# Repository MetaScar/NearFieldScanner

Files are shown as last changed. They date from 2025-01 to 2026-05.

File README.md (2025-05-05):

# Overview

Welcome to the low cost planar near-field scanner repo! 
The goal of this repo is to contain everything you will need to build your own near-field scanner.
Everything in this repo is open source under the Apache 2 license. Feel free to modify as needed, but reference this repo.

Instructions for how to build the near-field scanner are not yet complete. 
However, all the required parts for building the near-field scanner should be listed or an stl file provided to allow the user to 3D print their own parts.
Details on manufacturing these parts are not yet provided.

If you are interested in manufacturing your own near-field scanner, feel free to contact Jacob Stewart at jast5436@colorado.edu.

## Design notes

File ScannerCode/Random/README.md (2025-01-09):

Date: 2025-01-09
This folder is the result of organizing the code significantly later than when the code was created. This is random code with likely little importance to the end user. It is put here just in case the user is interested in looking.

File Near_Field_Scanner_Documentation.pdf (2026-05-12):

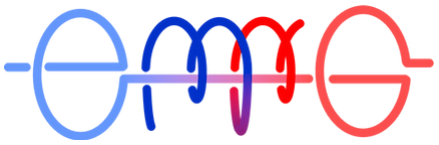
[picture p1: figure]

# Near Field Scanner Documentation

## Version 0.2

## Jacob Stewart

## Edited by Ellis Johnson

May 12, 2026

## Contents

### 1 Introduction | 2

### 2 Quickstart | 2

2.1 Common GRBL Commands | 2

### 3 Hardware | 2

3.1 General Comments | 2
3.2 Gantry System | 2
3.3 Panel Connection | 3
3.4 Circuit Design | 4
3.5 The Arduino Uno (GRBL) | 5
3.6 Cable Connections | 7
3.7 Comments and Improvements | 7

### 4 Software | 9

4.1 Definitions | 9
4.2 GRBL Commands | 9

### 5 Background Theory | 11

5.1 Near to Far Field Criteria | 11

### 6 Appendix | 11

6.1 GRBL Settings | 11

## List of Code Listings

# 1 Introduction

This documentation will cover the basics of how to use the near field scanner, how the hardware is configured, and how the software is configured. The hardware section will cover important things to note about the construction of the machine. Information that can likely be quickly understood by some quick analysis of the machine will probably be left out of the documentation.

# 2 Quickstart

## 2.1 Common GRBL Commands

# 3 Hardware

## 3.1 General Comments

Much of the design is based around CNC machines. The custom parts that deviate from this basic design (the panel and its connections, for example) will be covered in this manual.

The primary functions/aspects of the hardware are the GRBL Arduino Uno R3 controller, which controls the hardware for the gantry system, which holds and controls the position of the probe. The AUT is simply attached to an acrylic table.

## 3.2 Gantry System

The majority of the hardware components were purchased from OpenBuilds¹ (https://openbuildspartstore.com/)
. The remaining parts were likely custom designed. Parts can be found in the Microsoft Teams’ Near Field Scanner > Models folder.

1 https://openbuildspartstore.com/

Each of the linear rails can be constructed following this guide² (https://youtu.be/tLozVt_CjXQ?si=yefkdUC8tTgpIad6)
, which
demonstrates how to build a smaller version of the 1 meter (https://youtu.be/tLozVt_CjXQ?si=yefkdUC8tTgpIad6) linear actuators.

There are only two unique connections in the gantry system. The first is between the machine y-axis (the bar running between the parallel x-axis). Before making this connection, assemble the gantry plates, and attach them to the y-axis C-Beam. With how the x-axis C-Beams are attached to the wooden base, the gantry plates should be connected approximately 5 mm from the edges. Instead of tightening the attachment between the gantry plates and the y-axis C-Beam, keep them loose as you line up the gantry plates into the channels of the x-axis C-Beams. Unfortunately, the x-axis C-Beams are not perfectly parallel, so it is likely best to line up the gantry plates near the center of the x-axis C-Beams. Once the gantry plates are lined up to a satisfactory degree, you can tighten them in and run the lead screws through the gantry plates.

The other unique connection is between the gantry plate of the y-axis and the z-axis C-Beam. This requires a custom part, which is 3D printed from the “2 Become 1" model. There is a design for the smaller gantry plate and the larger gantry plate. For either plate, it is recommended to 3D print using and FDM printer. Though an SLA printer is more accurate, it also has a tendency to warp large flat surfaces. Additionally, the cost of SLA resin is much greater than FDM PLA filament.

Once the “2 Become 1" connector is printed, you must first attach the connector to the z-axis C-Beam. The screwing holes and method is the same as the C-Beam end mount. After the connector and the C-Beam are connected, you can attach the connector the y-axis gantry plate. You may want to ask for an assistant to hold the z-axis C-Beam while you are attaching the connector to the y-axis gantry plate.

## 3.3 Panel Connection

Many of the components for the panel system are removable. Unfortunately, in order to remove the panel completely from the z-axis gantry plate, nearly all the components must be disassembled one after

2 https://youtu.be/tLozVt_CjXQ?si=yefkdUC8tTgpIad6 the other. Those components include the “connect to panel" connector, the absorber, the acrylic panel, and the panel to z-axis connector.

In order to remove the panel, the absorber will need to be removed first. It is advised that two people work together to remove the absorber. It is also advised to wear gloves when handling absorber, as it can act as an irritant. To remove the absorber, carefully peel the velcro along the edges. When removing the absorber, something to avoid is damaging the absorber spikes.

These are fragile, and vital to the absorber’s performance. With this in mind, it is slightly better to start peeling the absorber from the velcro along the bottom edge and work your way up. If you were to drop the absorber while removing it from bottm to top, it is more likely to fall on the flat back of the absorber rather than the spiky front.

After the absorber has been removed, the acrylic panel can be unscrewed from the panel to z-axis connector. Once the acrylic panel has been removed and set aside, the panel to z-axis connector can be unscrewed and removed.

In order to remove the “connect to panel" connector, the absorber will need to be removed first, as described above. Though you can remove this part, it isn’t necessary. It is designed to remain attached, and instead provide screw holes for different probe to panel mounts. Each of these probe to panel mounts will have to be custom designed around the probe being connected. Each of these screw holes are evenly spaced 1.125 inches away from each other. An example 3D model of this part can be found in the “Probe to Panel Mount" file on Microsoft Teams.

Reassembly of the panel is mostly the same as removal in reverse. In particular, it is easier to install the absorber by connecting the velcro at the top of the panel, and work your way down, allowing the top connection to act as a hinge to swing the absorber into the remaining velcro connections.

## 3.4 Circuit Design

A wiring diagram can be found in Figure 1. Though the wiring may look like a complicated mess, if you look closely, the mess is a consequence of the amount of wires more than the complexity of the circuit. Most of

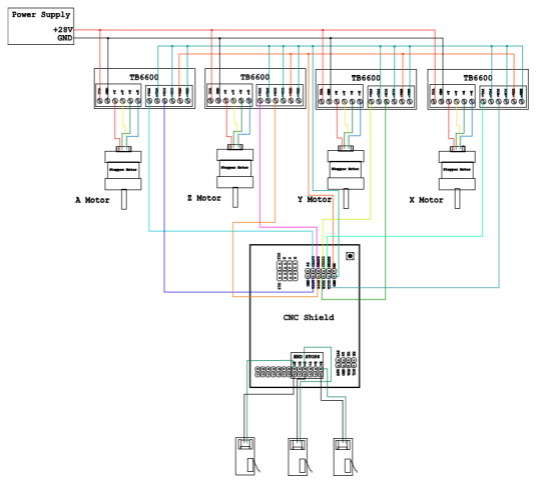
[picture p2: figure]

Figure 1: The CNC Wiring Schematic. Wire colors loosely match real wire colors, but are not perfectly equivalent.

the connections between the stepper drivers (the TB6600s) and the CNC Shield are for the CNC Shield’s ground pin.

As for the PCB design, the complete design file can be found in the Microsoft Teams folder in the file “PCB Wiring".

## 3.5 The Arduino Uno (GRBL)

The Arduino Uno is running a firmware called GRBL³ (https://github.com/gnea/grbl)
, which is a CNC
firmware that is practically the standard firmware for maker movement devices. Many 3D printers run GRBL under the hood. It is strongly advised to use an Arduino Uno R3 with a 16U2 communication chip rather than a CH340 chip. If you have the official Arduino Uno R3, you have the 16U2 communication chip. If you are not sure which chip your board has, it can be visually determined. On an official Arduino Uno R3, the 16U2 is the square surface mounted chip just behind the USB type-B port. On a board with a CH340 communication chip, in a similar location to the 16U2 chip, there will be a larger rectangular surface mounted chip.

3 https://github.com/gnea/grbl

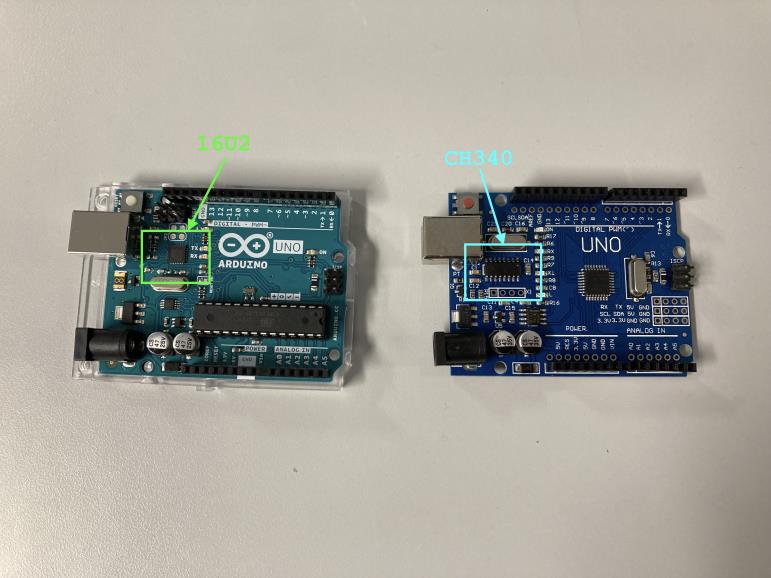
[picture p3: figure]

Figure 2: A visual comparison between the 16U2 chip and the CH340 chip. It is strongly advised to use an Arduino Uno R3 with the 16U2 chip.

When flashing the firmware to the Arduino Uno R3, there are two essential changes that need to be made to the GRBL configuration file. To make these changes, first follow the offical Compiling Grbl (https://github.com/gnea/grbl/wiki/Compiling-Grbl) 4 instructions up until step 5: “Compile and upload Grbl to your Arduino" for Arduino IDE 1.x, or until step 12 for Arduino IDE 2.x. At this point, the Grbl code has been added to your Arduino library.

In this library is the compilation configuration file. The essential changes will be made here. This file can be accessed by going to
WindowsUser/Documents/Arduino/libraries/grbl/config.h. | (Note | that
this location may change between your computer’s OS, the version of Arduino, etc. If you are unable to find the library, an internet search should allow for you to find the library location). For the first essential
change, | go | to | line | 124, | and | uncomment | #define
HOMING_SINGLE_AXIS_COMMANDS. For the second essential change, go to line 339 and comment out #define VARABLE_SPINDLE.

The first change is necessary because it enables commands that allow for each axis to be homed one at a time ($HX, $HY, $HZ). Homing each

4 https://github.com/gnea/grbl/wiki/Compiling-Grbl axis one at a time is more reliable than using the default in homing command $H. Thus, the Matlab code uses and requires these commands. The second change is necessary due to the CNC Shield in use. The newer version of GRBL uses pin D12 of the Arduino Uno rather than pin D11 for the Z-Axis limit switch. This is because the newer version of GRBL needs the PWM variable voltage output of D11 for a new feature to control a variable spindle. However, older versions of GRBL (which this CNC Shield had in mind) use pin D11 for the Z-Axis limit switch. Because this machine does not have a variable spindle and needs the Z-Axis limit switch, line 339 of the configuration file should be commented out to reenable pin D11 as the limit switch pin.

Once these configuration comments have been altered, you can flash the firmware.

After the firmware has been flashed, the GRBL settings need to be correctly configured. Open a serial connection with GRBL (for example, through the Arduino IDE) and check what settings are currently in use by the GRBL by entering $$. Change the settings as needed – the required settings can be found in Appendix 6.1. More information about the settings and how to change them can be found in the GRBL wiki⁵ (https://github.com/gnea/grbl/wiki/Grbl-v1.1-Configuration#grbl-settings) .

## 3.6 Cable Connections

There are two different connections that need to be made in order for the gantry system to be controlled. The first is the USB connection between the Arduino Uno R3 and the computer. This allows for the serial connection between the Arduino Uno and the computer for GRBL command communication. This also powers the Arduino Uno.

The second connection is the Cincon 28V AC power adapter. This connects between a wall outlet and the DC power jack on the wiring PCB. This powers the four TB6600 stepper drivers.

## 3.7 Comments and Improvements

Though the linear actuators⁶ (https://openbuildspartstore.com/c-beam-linear-actuator-bundle/) used for the gantry system are a cost effective method of getting a (approximately) millimeter precise machine,

5 https://github.com/gnea/grbl/wiki/Grbl-v1.1-Configuration# grbl-settings 6 https://openbuildspartstore.com/c-beam-linear-actuator-bundle/

they are not reliable as other methods. For example, a linear actuator combined with linear rails would be significantly more stable and reliable compared to just the linear actuator. With the inclusion of a feedback systems such as a PID control system, such a setup would likely be able to reach hundreds of micrometers of precision. Possibly even tens of micrometers. Such precision would allow for higher frequency measurements.

However, it is worth noting that such precision will not be necessary for the delta x criterion until frequencies above 200 GHz are being explored. Considering the hardware limitations of the VNA in use,

Another improvement would be the PCB design. The current design was made in house. For the sake of manufacturing convenience, vias were not added between the pins. Instead, the metal pins themselves were to act as the vias. To solder the top of the pin, solder paste was used. Unfortunately, the application and solidification of this solder paste was not very effective. This means the pins are incredibly susceptible to spontaneous disconnections. In other words, the PCB is not very reliable. This problem could be rectified by having a professional manufacture the PCB. As for a redesign, a PCB hat for the CNC shield would reduce the number of wire connections, keeping the package cleaner, more compact, and more reliable.

The AUT table is primarily lacking in one of the most important features for the table: its rigidity. The current design can easily be deflected, causing the entire table to oscillate. Fortunately, this oscillation is mostly caused by external forces, so while the machine is moving around when taking measurements, little oscillation occurs

The Z-Axis C-Beam also experiences a significant amount of wobble. The source of this wobble appears to be the gantry plate. A potential solution to this wobble would be to use a linear rail along the machine y-axis.

The power delivery method for the machine requires the user to manually plug and unplug the AC connector to wall power. It would be more convenient to power on the device with a switch. Along with this switch should be an emergency stop button which cuts power to the motors as soon as it is activated.

# 4 Software

## 4.1 Definitions

A confusing connection between the software and the hardware is the axis. In the software, you will see mentions of “machine x" or “code x". This is because what is the x-axis to the hardware (i.e., to GRBL) is different from the x-axis of the software. This is because much of the theory around transforming the near to far field of a planar near field scanner treats the distance between the probe and AUT as the z-axis, the horizontal motion between the probe and the AUT as the x-axis, and the height difference between the probe and the AUT as the y-axis. However, with how the hardware is configured, it is the x-axis that determines the distance between the probe and the AUT, the y-axis that determines the horizontal motion between the probe and the AUT, and the z-axis that determines the height difference between the probe and the AUT.

## 4.2 GRBL Commands

GRBL provides an explanation of the commands on the GRBL Wiki⁷ (https://github.com/gnea/grbl/wiki/Grbl-v1.1-Commands)
, and
though this manual will not cover all the commands, it will cover the most common ones used for this machine.

The first command the user will probably need to know is $X. This will unlock the machine, allowing the user to use subsequent commands to move the machine. The only other way to unlock the machine is with the homing commands.

If the user has followed the firmware flashing instructions in Hardware Section 3.5, then the special homing commands $HX, $HY, and $HZ can be used. These will home just their respective axis. Be careful when using this form of homing, as it will unlock the movement capabilities of the machine (same effect as $X) even if the other axis have not been homed. Thus, if your program requires all axis to be homed, either call all homing commands one after the other, or use the $H command (which has had spotty results for the current machine).

7 https://github.com/gnea/grbl/wiki/Grbl-v1.1-Commands

There are two basic homing commands: $G90 and $G91. Both of these commands have syntax in the form of:

$G91 X1 Y-2 Z3

(Quick Note: you don’t need to specify every axis every time you use the $G90 and $G91 commands. For example, $G91 X1 will only move the X axis, and will leave the Y and Z axis alone.)

The major difference between $G90 and $G91 is how it interprets the inputs for X1, Y2, and Z3. In the case of $G91, the machine is put into relative mode. This means if the user inputs X1, the machine will move the gantry system 1 unit in the positive X direction from its current X position. $G90, on the other hand, will move the machine to the absolute position where X = 1 unit. In the case of this particular machine, after the X axis has been homed, the absolute position is at -898.8 mm. This means that if the user were to input the command $G90 X1, the machine will attempt to ram the x-axis off the edge until it has “reached" the position at X = 1. In other words, it is generally much safer and easier for a person to use $G91 than it is to use $G90. However, absolute position is useful for programs and other aspects that don’t change between program reboots, such as the AUT position or the maximum and minimum positions of the axis.

Unfortunately, there doesn’t seem to be a command to stop the machine from making the current movement. Instead, the user will have to resort to hardware solutions, such as the ESTOP button on the PCB, or simply pulling the Arduino USB connection or pulling the power connection to the AC power supply connected to the PCB.

# 5 Background Theory

## 5.1 Near to Far Field Criteria

# 6 Appendix

## 6.1 GRBL Settings

The settings of the current GRBL setup after typing $$ into the GRBL serial prompt. More info on the GRBL settings can be found in the GRBL wiki⁸ (https://github.com/gnea/grbl/wiki/Grbl-v1.1-Configuration#grbl-settings)

Grbl 1.1h ['$' for help]
[MSG:'$H'|'$X' to unlock]
$0=10
$1=25
$2=0
$3=6
$4=0
$5=0
$6=0
$10=2
$11=0.010
$12=0.002
$13=0
$20=0
$21=0
$22=1
$23=3 $24=25.000
$25=500.000
$26=250
$27=1.000
$30=1000
$31=0
$32=0
$100=200.000

8 https://github.com/gnea/grbl/wiki/Grbl-v1.1-Configuration# grbl-settings

$101=200.000
$102=200.000
$110=500.000
$111=500.000
$112=500.000
$120=10.000
$121=10.000
$122=10.000
$130=900.000
$131=900.000
$132=900.000
ok

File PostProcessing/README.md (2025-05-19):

# Quickstart

The most powerful version of the post processing is contained in the `post_proc_nf_scan.m` Matlab file. By default, it uses the `NearFieldRawdata_Eravant_051525.mat` file located in the `./PostProcessing/Data/` directory. This file is provided in this GitHub repo as a link to a OneDrive as the file is around 600 MB (GitHub allows only a maximum of 100 MB before requiring [git-lfs](https://git-lfs.com/)). We do not use git-lfs due to our group's better familiarity with OneDrive compared to git.

With the post processing, the user can
- Time gate measurement by plotting both time and frequency domain
- Plot the near-field
- Plot the far-feild
- Plot the near-field radiation pattern to determine the phase center
- Plot the far-field radiation pattern 
- Plot 2D cuts at phi at 0, 45, and 90 degrees

Do be warned that the code can be quite memory hungry due to interpolation. To reduce memory usage by reducing interpolation, reduce the variable `N1q`.

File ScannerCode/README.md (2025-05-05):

Code related to or used by Professor Scarborough's Planar Near-Field Scanner. Majority of design and code created by Jacob Stewart. To communicate with a Keysight VNA, the code located in the "instrument" folder was created by Paul Flaten and Joel Johnson. Thank you for the code nerds!

# Quickstart
This quickstart guide is assuming you are trying to run the near-field scanner. This quickstart guide also assumes the user has arranged the antenna the user is testing (the AUT), and that the desired probe is installed. There is other code included in this repo that is used for just post processing the data located in the `./PostProcessing` directory. Hopefully, in a future version of the code, all post processing can be completed within the Matlab app. 

Because this guide is not exhaustive and perfect, if you think something is stupid/dangerous and you disagree with this guide, use your judgement. For example, if this guide does not tell you to wear an ESD strap while handling the VNA, but you think you should, use an ESD strap.

1. If you have not already, pull the git repo with desired method (using [GitHub Desktop](https://desktop.github.com/download/), the [terminal](https://github.com/git-guides/git-pull), etc.).
2. Start Matlab[^1], and turn on the VNA.
3. Inside Matlab, go to the directory of the git repo, then to `./ScannerCode`.
4. Inside Matlab, open `moveGUI.mlapp`. This is the Matlab app where the near-field scanner is controlled from.
5. The Matlab App Designer should have opened. Start the app by pressing the green play button up in the top left.
6. The app should be started. Now, plug in the Arduino Uno USB into the computer running the Matlab app and the <insert power block> into an outlet. If either does not seem to recieve power after plugging in, ensure the Arduino USB is connected to the USB-B port on the Arduino, and that the barrel connector is plugged into the PCB.
7. If you have not already, clear the space in and around the near-field scanner. It is about to start moving, so you don't want it to run into anything. Also, it is advised to unplug the probe and the AUT from the VNA, as future steps might cause electrical connections between the ports. Feel free to maintain the connection between the cable and the AUT/probe.
8. In the App, press the "Initialize" button in the top right. This will begin homing the machine.
9. Once the homing is completed and you have confirmed the completion, if this is the first time testing with the AUT positioned as it is now, you will need to run "Determine Z Dist" and "Find Probe Center". These will tell the program where the AUT is. If this has already been completed for the current setup, skip to step 12.
10. Click "Determine Z Dist". Follow the program, and use the controls to put the probe close to the AUT, and use a caliper to measure the physical distance between the probe and AUT. Write down the value provided by the program.
11. At the completion of "Determine Z Dist", you will be prompted to run "Find Probe Center". Go for it. Using the same controls, position the probe as close as possible to the center of the AUT. Write down the values provided by the program.
12. If you want the program to calculate the sampling criteria for a measurement, select "Determine Criteria". If you already have the criteria, skip this step.
13. Once you are ready to begin measuring, plug in the probe and AUT to the VNA.
14. Click "Run Measurement". The program will prompt you for anything it is missing, move to the center for one final check, then begin measuring.
15. At the completion of the measurements, you will be prompted to make a struct. This is advised, as variables such as the distance will be saved into the struct, which can be used later if you forgot how far the AUT was from the probe.
16. Once the measurement is complete, the data will be output to the `./ScannerCode/Data/` directory. Save this as preferred (e.g. USB drive, OneDrive, etc.).
17. Feel free to use the "Raw to Gated" program in the bottom right of the app to time gate your raw data, and "Raw to Struct" to turn the gated data into structs which can be used for plotting with the app's "Struct to Plots" program and transforming into the far field using the program `./PostProcessing/SimpleFarFieldTransform.m`.

# Data
It is not best practice to put your raw data files inside of git. Git is for tracking changes in text files. Instead, data files for the GitHub repo will be located in the [Microsoft Teams's `Files/Near Field Scanner/GitHubData` folder](https://o365coloradoedu.sharepoint.com/:f:/r/sites/ECEE-EMRG/Shared%20Documents/General/Near%20Field%20Scanner/GitHubData?csf=1&web=1&e=mdIfOC).
Folders named "Data" will be included in the git repo for the convenience of the user to put their own data. If there is data available in the Teams folder, it will be located in the same directory.
For example, the "Data" folder located at `./ScannerCode/Data/` is located at `/Near Field Scanner/GitHubData/ScannerCode` directory on Teams.

# Contact
Professor Cody Scarborough: cody.scarborough@colorado.edu

Jacob Stewart: jast5436@colorado.edu

Joel Johnson: jojo1082@colorado.edu

# Footnotes
[^1]: There are two different ways of starting Matlab apps. First, you do it through your file explorer without Matlab already opened. This will immediately open the app. The second is to open the app through Matlab's built in folder directory. In this case, the Matlab App Designer will also open up. This has the advantage of allowing the user to see the code (accessed by pressing "Code View" on the top right of the main window) and to see error messages. Because this code was made by an inept programmer and will likely produce many errors that require Matlab's error codes, it is advised to access the Matlab app through the Matlab App Designer.

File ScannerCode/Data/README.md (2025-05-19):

The current data files (M, O, S) are included as an example. You should not be including raw data in the git repo. 
This is enforced through the .gitignore file.

For the EMRG group, the data can be found in the [Teams Folder](https://o365coloradoedu.sharepoint.com/:f:/r/sites/ECEE-EMRG/Shared%20Documents/General/Near%20Field%20Scanner/GitHubData?csf=1&web=1&e=lnERgP).

Other teams/individuals are free to use [git-lfs](https://git-lfs.com/) or their own choice of file hosting to share the data files.

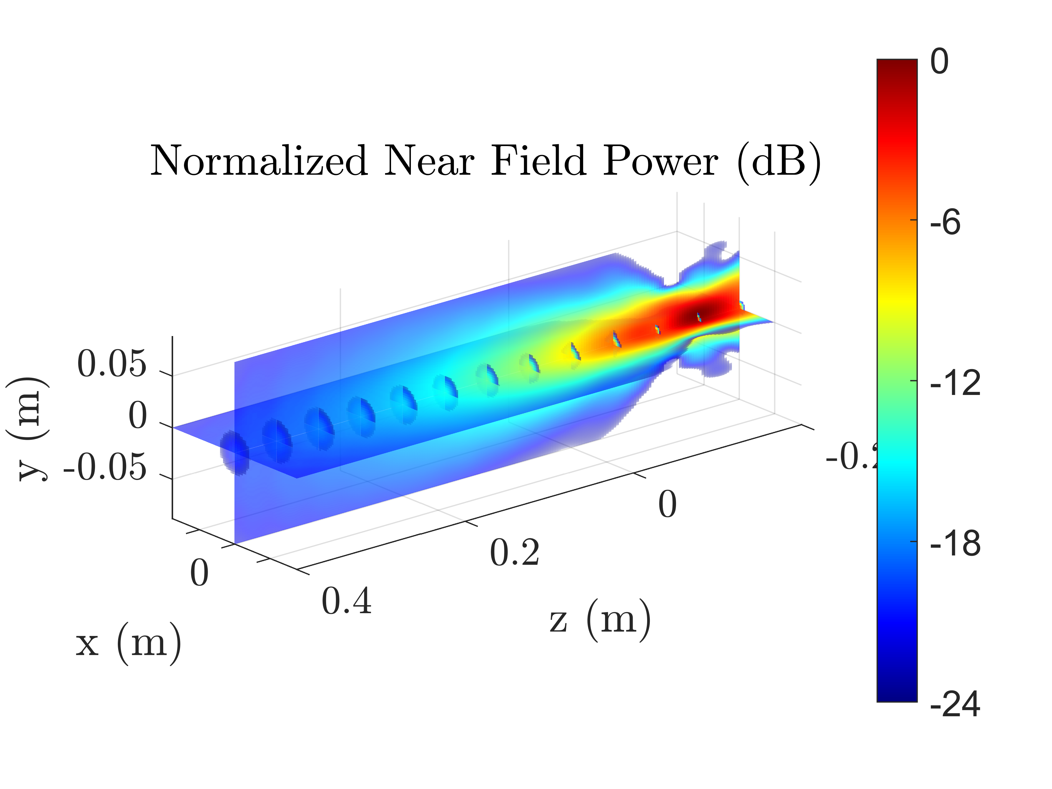
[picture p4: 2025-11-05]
PostProcessing/NearFieldProfile.png

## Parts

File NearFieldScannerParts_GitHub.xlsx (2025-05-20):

Item | Link | Number of units
WR90 open ended waveguide probe | https://www.ebay.com/itm/315099929331 | 1
Linear actuator (1m) | https://us.openbuilds.com/c-beam-linear-actuator-bundle/ | 3
10 ft mini circuit SMA cable | https://www.minicircuits.com/WebStore/dashboard.html?model=ULC-10FT-SMSM%2B | 1
6 ft mini circuit SMA cable | https://www.minicircuits.com/WebStore/dashboard.html?model=ULC-6FT-SMSM%2B | 1
Absorber: AEMi AEP-04 LG | https://www.mvg-world.com/en/products/absorbers/standard-absorbers/pyramidal-absorbers-aep-series | 1
CNC controller kit | https://www.amazon.com/Twotrees-Controller-Stepper-8-0%EF%BC%8CTB6600-Board%EF%BC%8CSwitch/dp/B08XNQTQXN | 1
40x40 Aluminum extrusion | https://us.openbuilds.com/v-slot-40x40-linear-rail/?searchid=0&search_query=aluminum+extrusion | 2
Aluminum extrustion corner brackets | https://www.mcmaster.com/products/aluminum-extrusion-gussets/t-slotted-framing-rail-profile~quad/rail-height~20-mm/ | 4
Acrylic sheet 24" x 24" | https://www.amazon.com/Acrylic-Plexiglass-Perspex-Transparent-Sheeting/dp/B07ZJM5GTP | 1
Arduino | https://store-usa.arduino.cc/products/arduino-uno-rev3?selectedStore=us | 1
Acrylic rods | https://www.amazon.com/FixtureDisplays%C2%AE-Diameter-Plexiglass-Transparent-10132-24/dp/B09T69KKSM?s=industrial | 4
M5 nuts | https://us.openbuilds.com/low-profile-screws-10-pack/ | 4
M5 Aluminum V nut pack | https://us.openbuilds.com/tee-nuts-m5-pack/ | 1
Drag Chains | https://www.amazon.com/Flexible-Connectors-Screwdriver-Engravers-Woodworking/dp/B09JCD362N | 2
1m V-Slot 40x40 | https://openbuildspartstore.com/v-slot-40x40-linear-rail/ | 2
Extended Open Gusset (5537T663) | https://www.mcmaster.com/products/aluminum-extrusion-gussets/t-slotted-framing-rail-profile~quad/rail-height~20-mm/ | 4

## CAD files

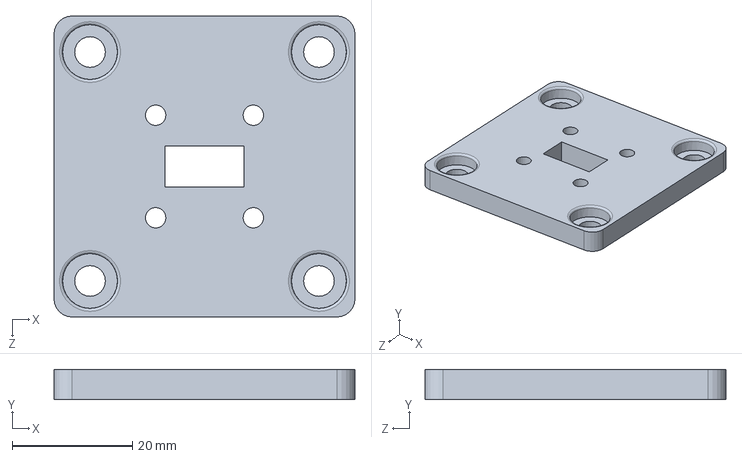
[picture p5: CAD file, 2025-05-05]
CAD/Original/Probe/WR42ProbeToPanelMount.SLDPRT
50.1 x 5.00 x 50.1 mm

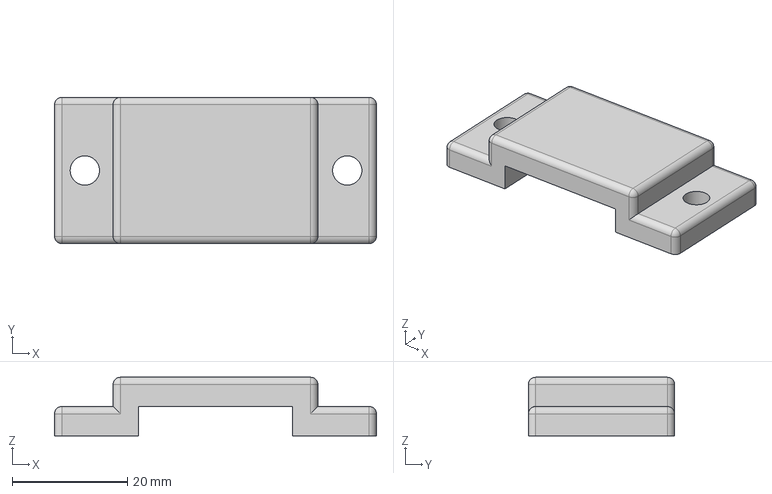
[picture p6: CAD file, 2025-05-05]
CAD/STEP/AUT/WR90GrabberTop.step
55.9 x 25.4 x 10.2 mm

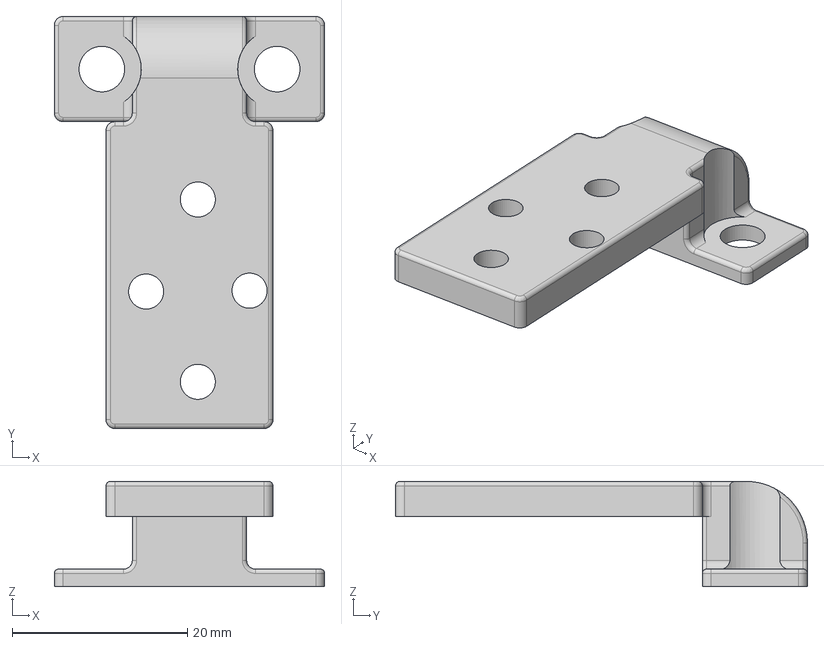
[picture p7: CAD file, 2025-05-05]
CAD/STEP/Wiring/XAxisDragChainConnector.step
30.8 x 47.0 x 12.0 mm

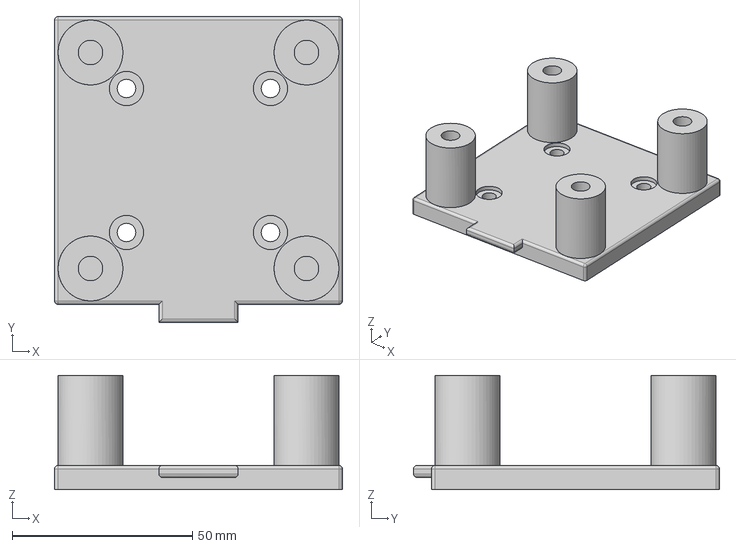
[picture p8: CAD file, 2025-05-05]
CAD/STEP/Z-AxisMount/ZAxisToPanel.step
80.0 x 85.0 x 31.7 mm
Panel

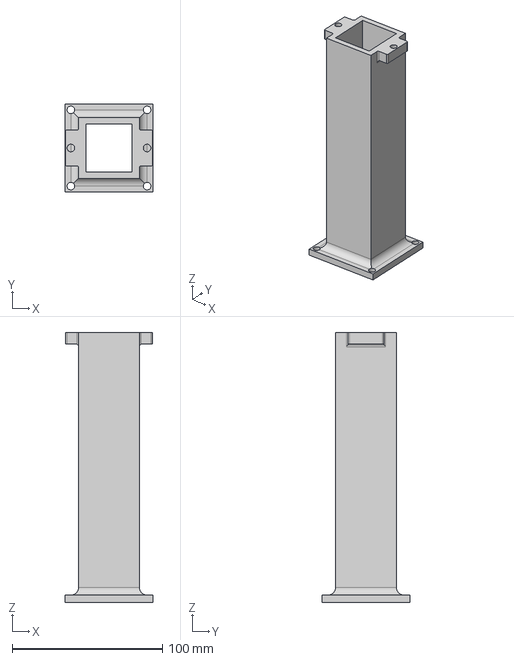
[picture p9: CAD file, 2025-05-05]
CAD/STEP/AUT/AUT Booster Seat v2.step
58.4 x 58.4 x 180.0 mm

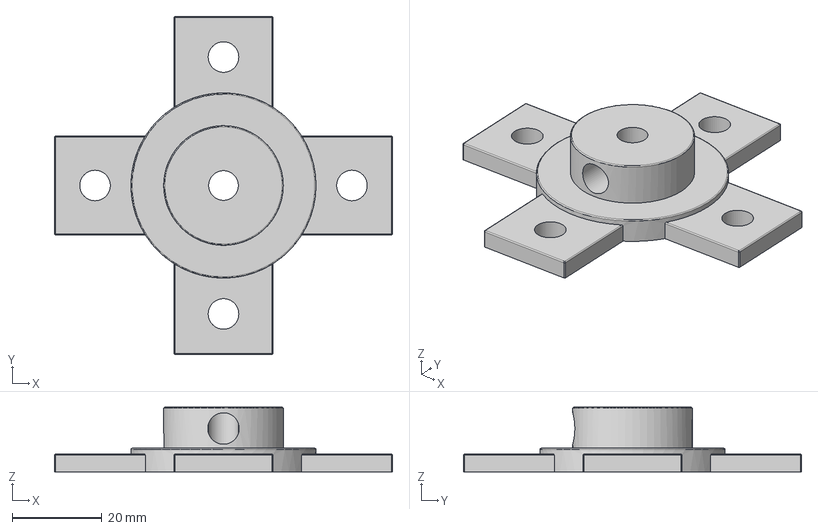
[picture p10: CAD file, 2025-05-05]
CAD/STEP/Probe/PigtailProbePanelMount.step
75.2 x 75.2 x 14.4 mm

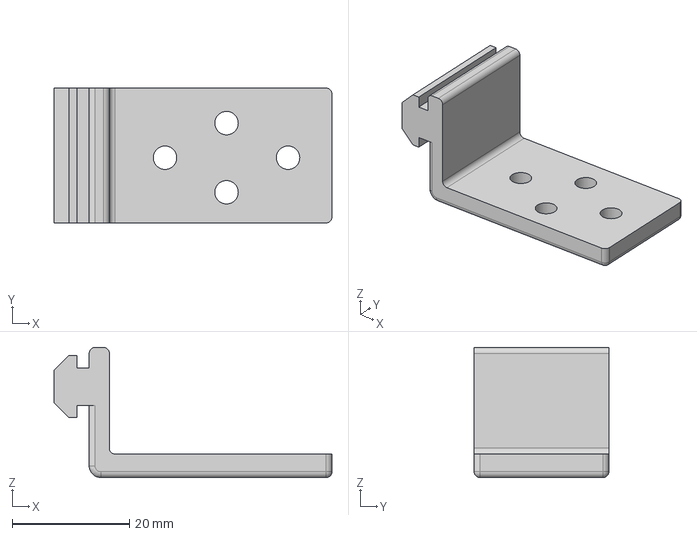
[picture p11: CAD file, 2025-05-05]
CAD/STEP/Wiring/YAxisDragChainHolder.step
47.5 x 23.0 x 22.2 mm

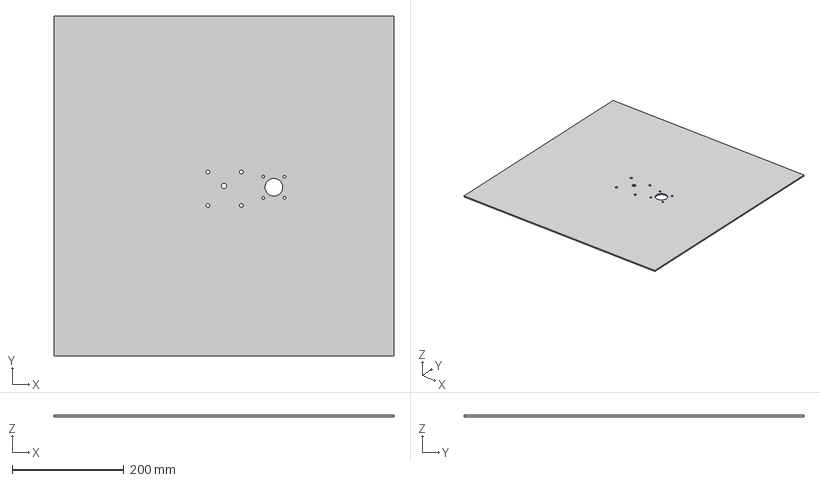
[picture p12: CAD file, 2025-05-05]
CAD/STEP/Z-AxisMount/AcrylicPanelCutout.step
609.6 x 609.6 x 3.18 mm

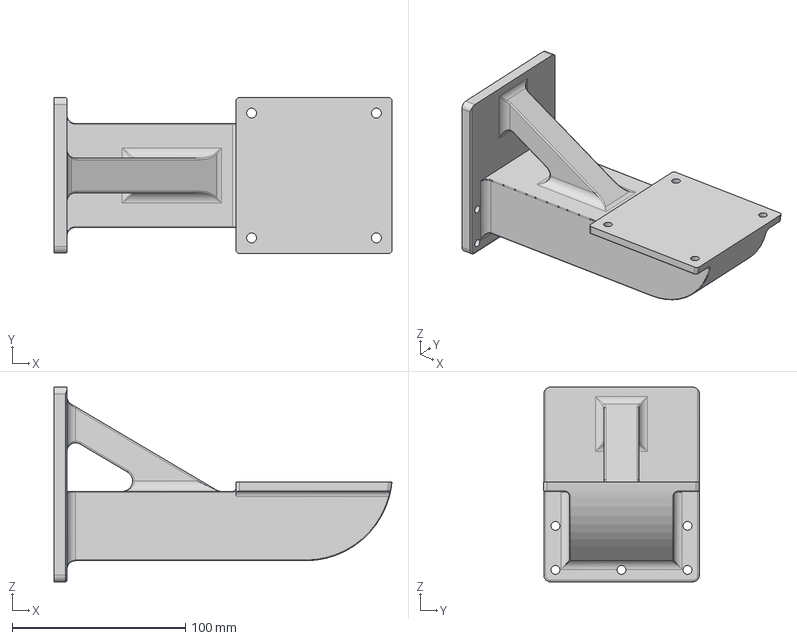
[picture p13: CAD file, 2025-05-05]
CAD/STEP/AUT/EravantAUTHolder v13.step
195.0 x 90.0 x 112.4 mm

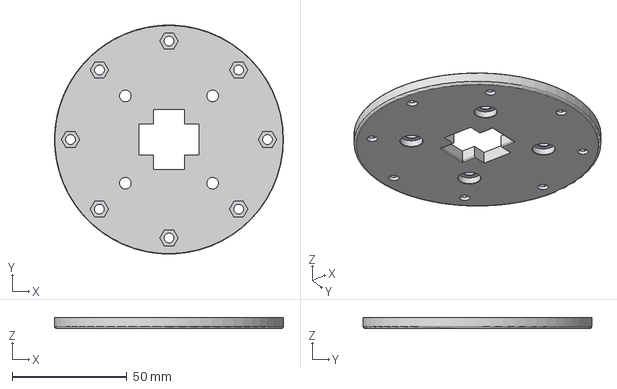
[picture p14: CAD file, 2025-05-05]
CAD/STEP/Probe/WR90OpenEndedWaveguideProbeMount.step
100.0 x 99.9 x 5.00 mm

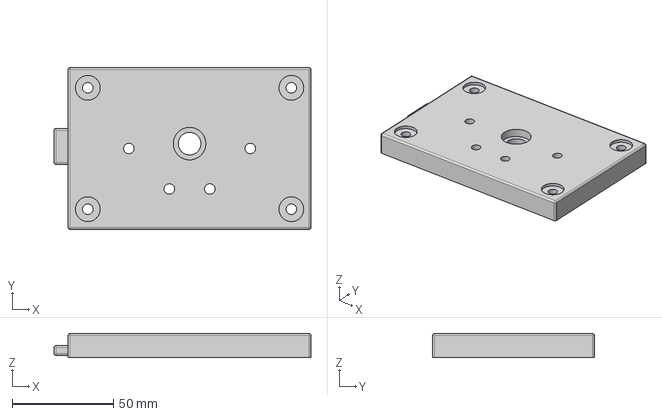
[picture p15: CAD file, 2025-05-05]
CAD/STEP/Z-AxisMount/Large 2 Become 1 v5.step
127.0 x 80.0 x 12.0 mm

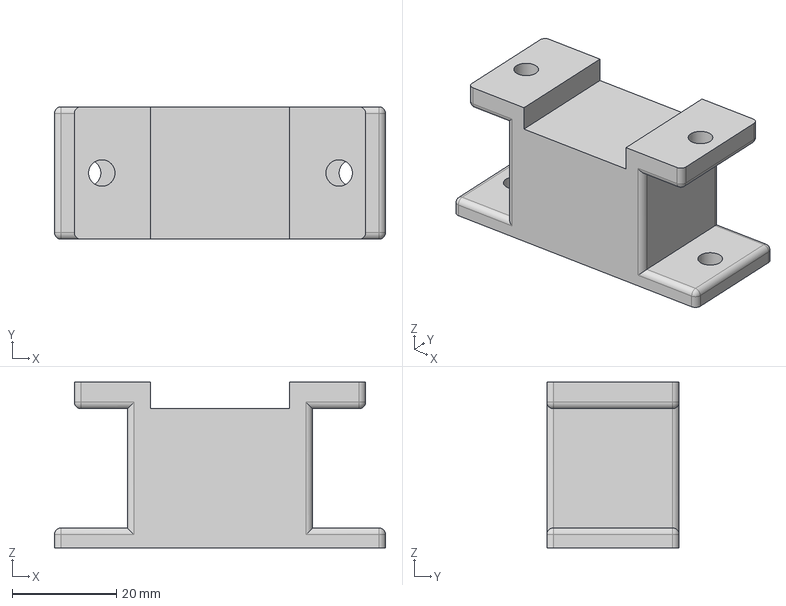
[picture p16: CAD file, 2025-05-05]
CAD/STEP/AUT/WR90GrabberBottom.step
63.5 x 25.4 x 31.8 mm

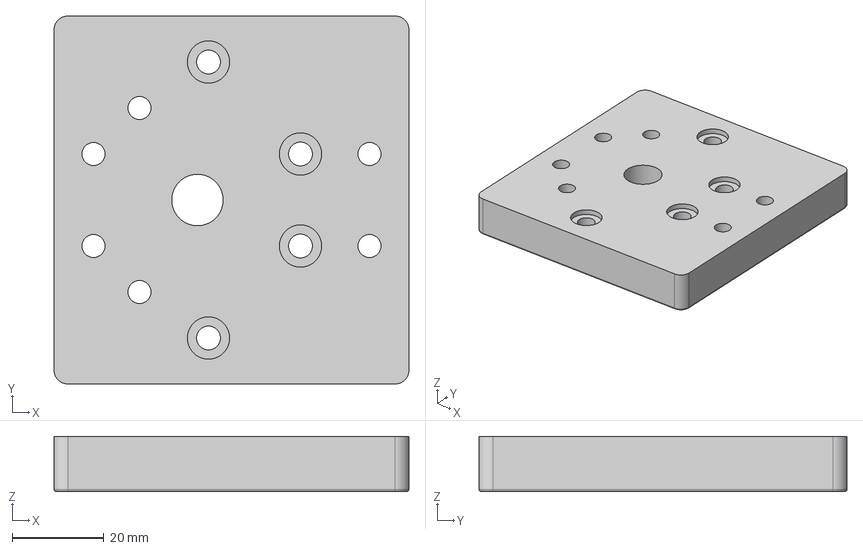
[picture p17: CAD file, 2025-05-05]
CAD/STEP/Z-AxisMount/2 Become 1 v9.step
77.2 x 80.0 x 12.0 mm

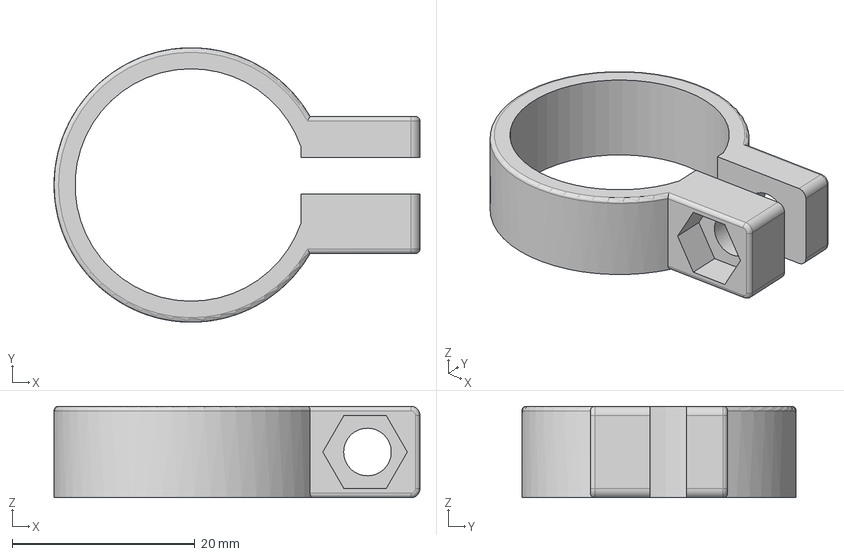
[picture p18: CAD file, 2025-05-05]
CAD/STEP/AUT/3D Shaft Collar v7.step
40.0 x 30.0 x 10.0 mm

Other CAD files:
CAD/STEP/Probe/WR42ProbeToPanelMount.STEP
CAD/Original/AUT/3D Shaft Collar v7.f3d
CAD/Original/AUT/AUT Booster Seat v2.f3d
CAD/Original/AUT/EravantAUTHolder v13.f3z
CAD/Original/AUT/WR90Grabber v6.f3z
CAD/Original/Probe/PigtailProbePanelMount.f3z
CAD/Original/Probe/Probe Mount Face On v27.f3z
CAD/Original/Probe/WR90OpenEndedWaveguideProbeMount.f3z
CAD/Original/Wiring/CableTrack v23.f3z
CAD/Original/Wiring/PCB Wiring v29.f3z
CAD/Original/Z-AxisMount/2 Become 1 v9.f3z
CAD/Original/Z-AxisMount/Large 2 Become 1 v5.f3z
CAD/STL/AUT/3D Shaft Collar v7.stl
CAD/STL/AUT/AUT Booster Seat v2.stl
CAD/STL/AUT/WR90GrabberBottom.stl
CAD/STL/AUT/WR90GrabberTop.stl
CAD/STL/Probe/PigtailProbePanelMount.stl
CAD/STL/Probe/WR42ProbeToPanelMount.STL
CAD/STL/Probe/WR90OpenEndedWaveguideProbeMount.stl
CAD/STL/Wiring/XAxisDragChainConnector.stl
CAD/STL/Wiring/YAxisDragChainHolder.stl
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

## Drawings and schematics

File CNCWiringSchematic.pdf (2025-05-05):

TB6600
TB6600

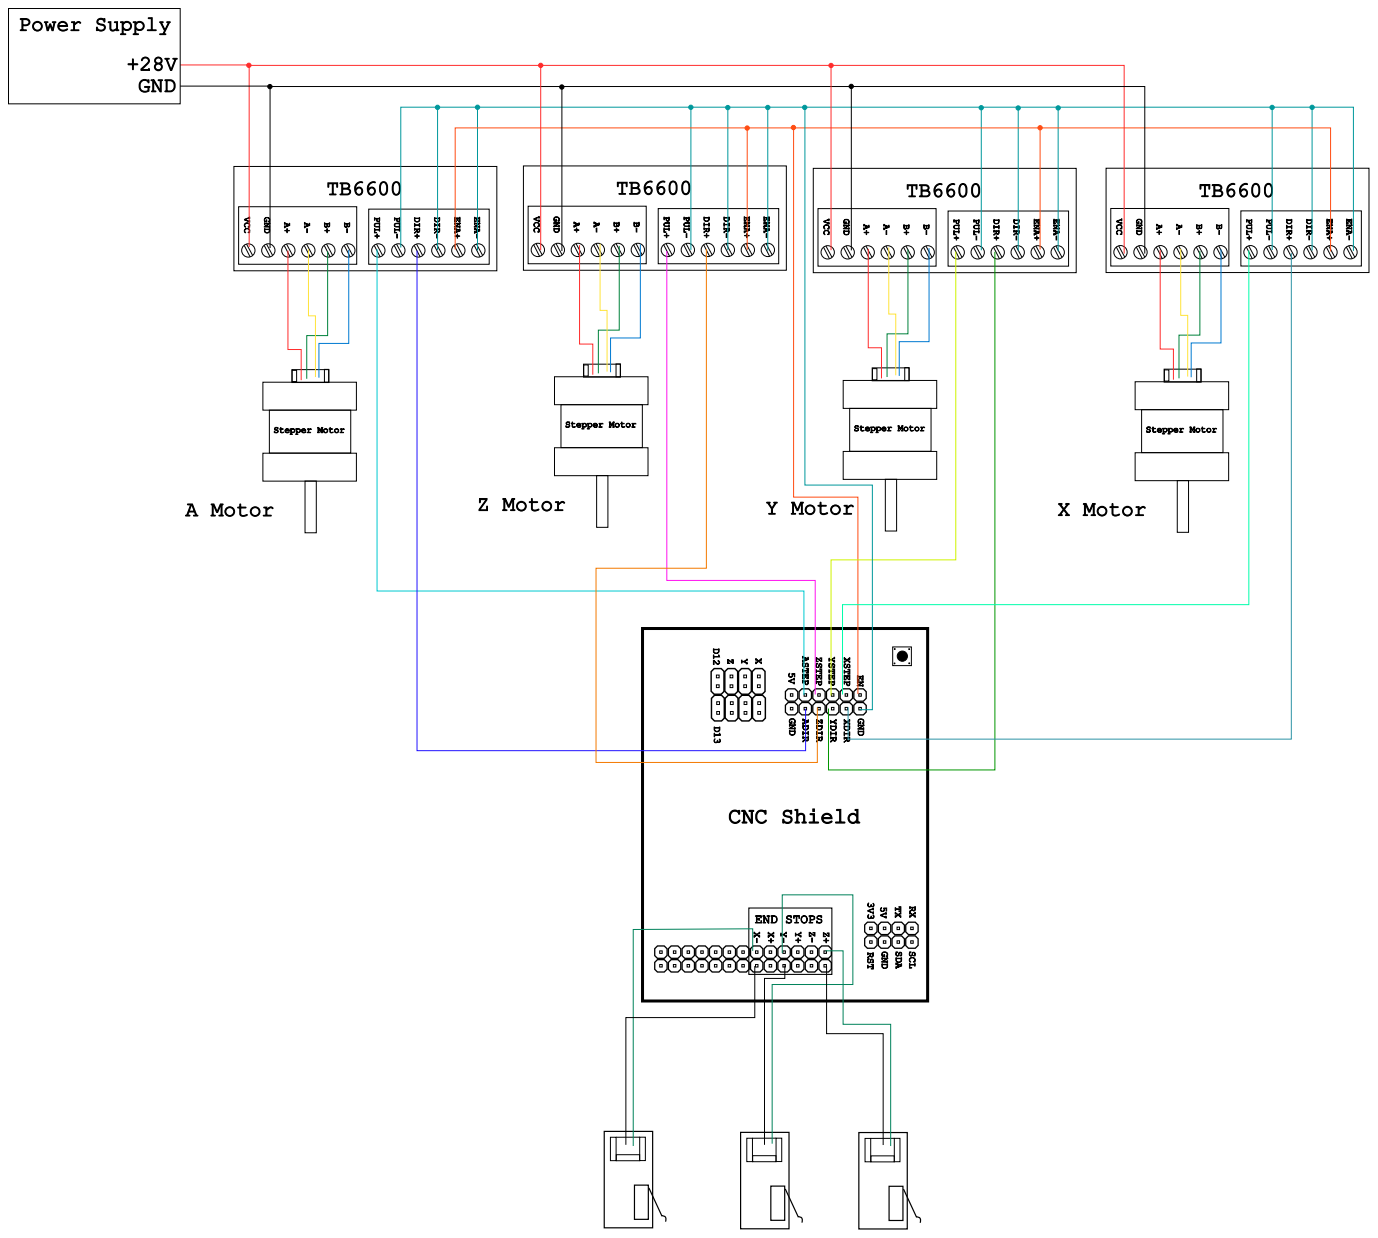
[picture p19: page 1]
END; STOPS; CNC Shield; Stepper Motor; A Motor; Z Motor; Y Motor; X Motor; Power Supply; +28V GND

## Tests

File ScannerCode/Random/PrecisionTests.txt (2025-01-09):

LX
T1: +20 mm
Result: +20.27 mm

LR
T1: +20 mm
Result: +20.27 mm

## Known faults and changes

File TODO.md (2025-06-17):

## Things to do for the git repo

- Complete the quickstart guide (including how to turn on, plug in, time gate, etc)
- Review quickstart guide, making sure it's all in second person
- Quickstart guide photos

## Things to do in NearFieldScanner code
- Fix calculate parameters code
- Add windowing before and after IFFT and FFT in time gating code to reduce spectral leakage
- Add built in far field transforms
- Add probe compensation option
- Add probe compensation back to near field option
- Add an option (if the connection to Arduino fails) to type in the COM number of Arduino (COM3, COM6, etc.)

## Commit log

2024-07-03 Improvements and function additions Add comments on machine current status (connecting, progress, etc) Home at end of program Corrected the error commands of y_positon function Debugged Z-position fu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
2024-07-23 Add code in txt file (for better tracking if current code is pasted in). Move gui added functionality for converting raw matlab data into struct and presenting struct to mag and phase plots
2025-01-09 organize current code in the repo
2025-05-05 CAD start
    [2 Become 1 v9.f3z, 3D Shaft Collar v7.f3d, AUT Booster Seat v2.f3d, CableTrack v23.f3z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]
2025-05-05 all step, stl files available. Added EravantAUTHolder to original files, and updated pigtail and wr90 open ended files
    [2 Become 1 v9.step, 2 Become 1 v9.stl, 3D Shaft Collar v7.step, 3D Shaft Collar v7.stl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]
2025-05-05 added eravant wr42 probe mount from Solidworks
    [WR42ProbeToPanelMount.SLDPRT, WR42ProbeToPanelMount.STEP, WR42ProbeToPanelMount.STL]
2025-05-05 rearrange readmes, add CAD files for drag chains and panel to z axis mount
    [AcrylicPanelCutout.step, AcrylicPanelCutout.stl, XAxisDragChainConnector.step, XAxisDragChainConnector.stl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]
2025-05-05 add most current version of documentation
2025-05-20 update parts list
    [NearFieldScannerParts_GitHub.xlsx]
